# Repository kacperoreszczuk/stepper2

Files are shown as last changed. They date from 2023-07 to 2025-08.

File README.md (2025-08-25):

# stepper2
Second version of the lums stepper

Compiling in STM32CubeIDE:

0. Disclaimer: STM32CubeIDE constantly invents new ways to make this instruction not work. Be mentally prepared that you will have to bruteforce this with LLM anyway.
1. Install STM32CubeIDE, sadly requires account creation
2. Click "Import project" and select "fw" directory from this repository
3. In the "Project Explorer" panel on the left open stepper2.ioc
    - confirm "open associated perspecitve" if prompted
    - continue with the current version of the firmware if prompted (do not migrate)
    - Login into MyST account if prompted
    - if not prompted and you get problems later in the instruction in point 4  (more precisely "this project is not a CDT project") then in the stepper2.ioc window click Help->Configuration Tool->Manage Embedded Software Libraries, scroll to STM32H7 and check tick box near version 1.11.1. Click Install. Hopefully you will be prompted to login and the package will install. Continue with instruction (starting here with Project->Generate Code)
    - in the top menu select Project->Generate Code
    - confirm "open associated perspecitve" if prompted
4. go to Project -> Properties -> C/C++ Build -> Settings
    - if "Properties" button is inactive click on main.c file subwindow to focus on it
    - in MCU(or MCU/MPU) Settings  check both "Use float..." options
    - in "MCU Post build outputs" enable binary file (or "convert to binary file")
    - in MCU(or MCU/MPU) GCC Compiler->Optimization: change level to -O3
    - in MCU(or MCU/MPU) G++ Compiler->Optimization: change level to -O3
    - If you want to switch to release configuration, change configuration to Release in the top of the Settings window, and repeat last four steps. In that case take care to build in the release later.
    - click apply and close, confirm if prompted to rebuild index
5. You may want to go to Core/Inc/defaults.hpp and change #define DRIVER_ID to a different value (any you like), especially if you would use more than one device simultaneously and want to be able to discern between them when talking through serial port.
6. Power up the driver and connect it with micro usb port (near the power input socket, slightly lower). Click Run->Run or click the green arrow icon to build and flash the device.
    - You may be prompted to upgrade the stlink firmware. Agree. In the STLinkUpgrade Window click "Open in update mode" and then "Upgrade". Unplug and plug the micro USB cable and try again number 6 in this instruction.
    - you may be prompted to save the files you edited. Agree.
7. Alternatively to point 6. you can select Project->Build Project and then copy manually the file in Debug/stepper2.bin to the mass storage device that opens after conneting the driver.

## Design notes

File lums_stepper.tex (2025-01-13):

%

\documentclass[10pt,article]{article}
\usepackage[T1]{fontenc}
\usepackage[utf8]{inputenc}
\usepackage{graphicx}
\usepackage{hyperref}
\usepackage[font={small,it}]{caption}
\usepackage[a4paper,top=1.1cm,bottom=2cm,left=1.9cm,right=1.9cm]{geometry}
\usepackage{color, colortbl}
\usepackage{tabularx}
\usepackage{sectsty}
\usepackage{float}
\usepackage{hyperref}
\definecolor{Gray}{gray}{0.85}
\sectionfont{\huge}
\renewcommand{\familydefault}{\sfdefault}
\captionsetup{labelfont=bf}

\title{LUMS Stepper 2.0 -- universal 3-axis stepper motor controller}
\author{Kacper Oreszczuk}
\date{}
\begin{document}

\maketitle
 \section{Motivation}
Stepper motors are commonly used in laboratory. They are powering x-y-z translation stages, tunable filters, polarisation optics and many other devices. The goal of this project is to replace commercially available drivers with a cheaper, more reliable and more universal solution. 

\subsection*{Cost:}
Commercially available stepper motor drivers designed for laboratory use can reach prices
of a few hundred US\ Dollars for a single axis. Proposed solution costs about \$40 per axis with small
labour cost.

\subsection*{Quality:}
Personal experience in our laboratory revealed problems with microstep precision in drivers supplied by one of the leading laboratory equipment manufacturers. I have tested thoroughly stepper motor chip before choosing it for this project. 
\subsection*{Features:}
Custom solution allowed me to implement important additional features. The most important is automatic compensation of mechanical hysteresis.

\section{Hardware design}

Single device is able to control three bipolar stepper motors with 1/64 microsteps precision. Maximum current is about $2.0$\,A per motor and the supply voltage must be between $7$\,V and $24$\,V.
Low level motor driving operation  is performed by\textit{TMC2226} driver on \textit{Stepstick} breakout board. Three such drivers are connected to \textit{NUCLEO144}  board with \textit{STM32H723ZG} microcontroller. Nucleo board connected via on-board \textit{FT232RL}\ USB-UART controller to computer provides virtual serial port for communication and power for logic layer of device. Separate power connector is provided on main PCB for motor operation and six high-density D-SUB15 female connectors for motors and encoders. Full schematics of the device is presented in Figure \ref{schematics}. PCB board is double-sided. It is advised to order PCB with SMD\ assembly. See Figure \ref{pcb} for PCB layout.  The driver is confined in 3D-printed case (Figure \ref{case}) protecting it and allowing mounting to optic table. 
%Picture \ref{photo} shows assembled device with the top lid removed. 
Design files for PCB and case along with source code for microcontroller are available at project page: \url{github.com/kacperoreszczuk/stepper2/}. 

%\begin{figure}[h] \centering \includegraphics[width = 11.5cm]{photo.png}
%\caption {Assembled Stepper 2.0.} \label{photo}\end{figure}
\newpage
\section{Software and protocol}

Driver has two basic operation modes - movement with given velocity or movement to given position. In either of the cases the movement of motor is smoothed at starting and stopping. For user convenience speeds and positions are expressed in real units (for example millimeters in case of linear travel stage), not motor steps. End switches (limit switches) of different types are supported by this driver. They provide additional safety, as the driver will stop at the edge of the movement range of, for example, linear translation stage. Limit switches are also used to automatically calibrate absolute position of the stage.

When the mechanical setup of driven actuator is not completely rigid, the mechanical hysteresis can occur. Due to this effect real position of the  actuator depends on the direction from which set position is approached. In this project user can specify the amplitude od mechanical hysteresis. Algorithm will track previous movements and compensate the offsets in a manner transparent for the user.  

User can communicate with LUMS Stepper via virtual serial port provided by Nucleo board. Protocol of communication is based on single line plain-text commands initiated from computer and on single line reply from driver. For protocol description please refer to Table \ref{protocol}. Full list of accepted commands is presented in Table \ref{commands}

\begin{table}[ht]\centering
\begin{tabularx}{\textwidth}{lX}
\rowcolor[gray]{0.80} Command: & ID header value \textbackslash r \\
\rowcolor[gray]{0.95} ID & Single digit number – number of motor, counted from 0. Defaults to 0 if not specified.\\
\rowcolor[gray]{0.95} header & Two lower case characters specifying command type (see table \ref{commands}).\\
\rowcolor[gray]{0.95} value & Numerical argument (optional depending on command type). Defaults to 0 if not specified. \\
\rowcolor[gray]{0.95} \textbackslash r or \textbackslash n\ & Any endline character. Other whitespace before, after or between command parts is ignored. \\
\rowcolor[gray]{0.80} Reply: & header value \textbackslash r\\
\rowcolor[gray]{0.95} header & Driver returns header after every command \\
\rowcolor[gray]{0.95} value & Optional depending on command type\\
\rowcolor[gray]{0.80} Error reply: & ?\textbackslash r\\
\end{tabularx}
\caption{Protocol of communication between PC and LUMS\ Stepper 2.0.}\label{protocol}
\end{table}

\begin{table}[ht] \centering
\begin{tabularx}{\textwidth}{lllX}
\rowcolor[gray]{0.80} Command & Abbreviation origin & Example & Description\\
\rowcolor[gray]{0.90} id & ID & id & Returns unique ID of device, between 101 and 199.\\
\rowcolor[gray]{0.95} ac & Axis Count & ac & Returns number of supported motors.\\
\rowcolor[gray]{0.90} sc & Set Current & 0sc600 &Sets motor current, in milliamperes.\\
\rowcolor[gray]{0.95} ss & Set Step & 0ss0.005 & Defines the size of motor full step in user units, for example in millimetres or degrees. \\
\rowcolor[gray]{0.90} sh & Set Hysteresis & 0sh0.001 & Sets mechanical hysteresis compensation distance. Algorithm applies corrections to target positions when necessary (f. eg. when changing direction). \\
\rowcolor[gray]{0.95} sm & Set Max Velocity & 0sm1.5 & Sets maximum allowed velocity in move velocity mode, in user units. \\
\rowcolor[gray]{0.90} sv & Set Velocity & 0sv1 & Sets velocity in move absolute mode, in user units. \\
\rowcolor[gray]{0.95} sa & Set Acceleration & 0sa0.5 & Sets time that it takes to accelerate from zero to move absolute velocity. \\
\rowcolor[gray]{0.90} sl & Set Limit & 0sl2 & Sets limit switch type. 0 – no limit switch, 1 - active limit switch (active high). 2/3 – mechanical, default NC/C. 4/5 similarly to 2/3, but enabled only for homing. \\
\rowcolor[gray]{0.95} sr & Set Reversed & 0sr1 & Reverses direction of motor rotation and swaps limit switches. \\
\rowcolor[gray]{0.90} so & Set Offset & 0so4.2 & Specifies the true position of the limit switch in user units. \\
\rowcolor[gray]{0.95} hm & HoMe & 0hm & Starts homing procedure. If limit type is set to zero, then it only corrects current position to be zero. \\
\rowcolor[gray]{0.90} hr & Homing Reversed & 0hr1 & Specifies if homing should be performed to rear limit switch (0, default) or to front limit switch (1).\\
\rowcolor[gray]{0.95} mv & Move Velocity & 0mv0.5 & Sets target velocity. Driver will smoothly increase or decrease speed to given value. \\
\rowcolor[gray]{0.90} ma & Move Absolute & 0ma3.2 & Sets target position. Driver will smoothly start and halt motor to achieve goal position. \\
\rowcolor[gray]{0.95} mr & Move Relative & 0mr0.1 & Changes target position by given value, even if target position was not achieved yet. In „move velocity” mode sets target relative to current position. \\
\rowcolor[gray]{0.90} tp & Tell Position & 0tp & Returns current position of given axis. \\
\rowcolor[gray]{0.95} ts & Tell Status & 0ts & Returns status of current axis. 0 – stopped, 1 – move velocity, 2 - move position, 3 – homing. \\
\rowcolor[gray]{0.90} ta & Tell All & ta & Returns current positions of all axes, separated by spaces. Next, after another space, returns statuses of all axes in single joined string.\\
\rowcolor[gray]{0.95} er & Encoder Raw & 0er & Returns encoder position in raw counts.\\
\rowcolor[gray]{0.90} es & Encoder Step & 0es0.002 & Configures encoder step in user units. Must be called after configuring motor step.\\
\rowcolor[gray]{0.95} ep & Encoder Position & 0ep & Returns encoder position in user units. \\
\rowcolor[gray]{0.90} ds & Driver Status & 0ds & Returns the TMC's DRV\_STATUS register in hex format. See TMC2226 datasheet, table 5.5.3 for details. \\
\rowcolor[gray]{0.95} dr & Driver Reset & 0dr & Cycles the EN pin of the TMC driver, clearing the hardware error flags in the process. \\
\rowcolor[gray]{0.90} tt & Tell Time & tt & Returns time from boot in seconds. \\
\end{tabularx}
\caption{Commands in communication protocol.}\label{commands}
\end{table}

\begin{figure}[H]
 \centering
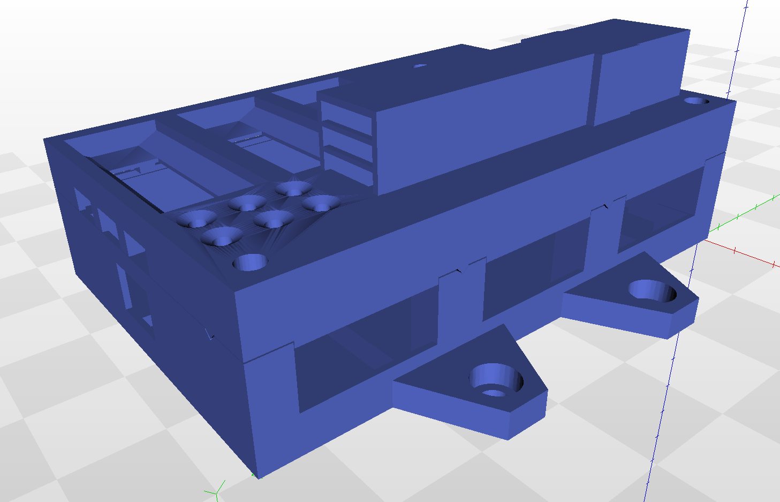
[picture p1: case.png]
 
\caption {Case, model for 3D printer.} \label{case}
\end{figure}

\begin{figure}[h]
 \centering
 
\caption {Schematics of the LUMS stepper.} \label{schematics}
\end{figure}

\begin{figure}[h]
 \centering
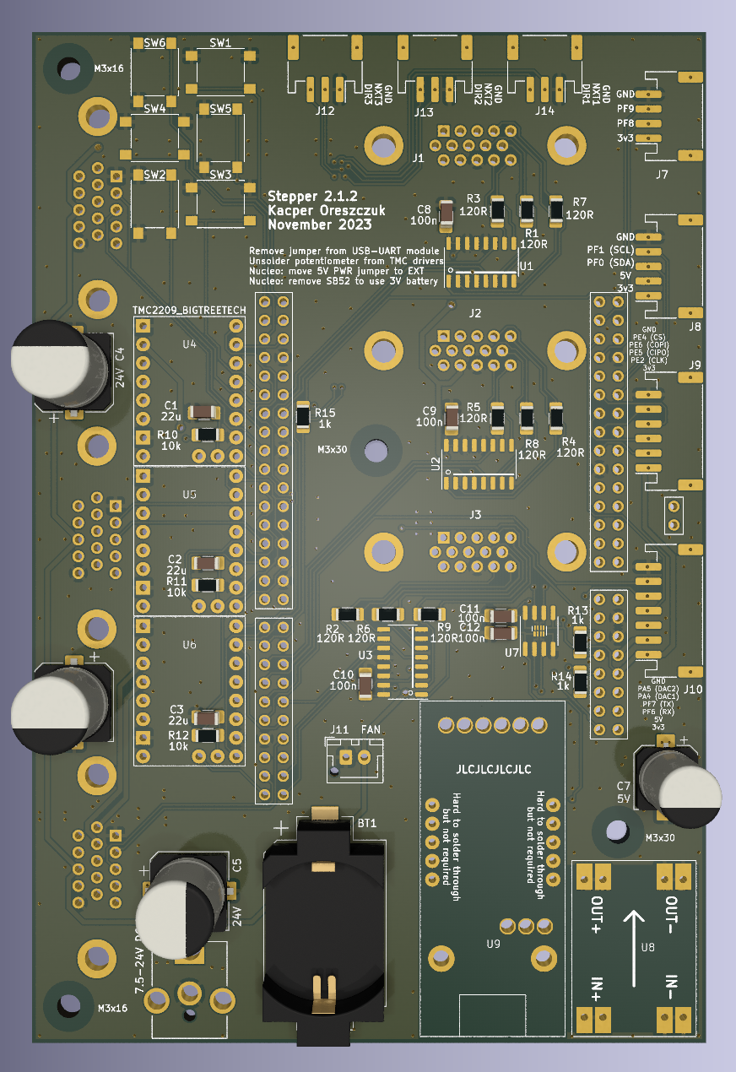
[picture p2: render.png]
 
\caption {PCB design. View from top.} \label{pcb}
\end{figure}

\newpage
\section{How to set-up Stepper 2.0 in pyLUMS software}
This section is very specific to LUMS laboratory.

In order to control Stepper 2.0 from pyLUMS software, you need to configure it in \texttt{local\_devices.ini} and \texttt{devices.ini} file. Most of the work is put in the former one. Here is example of the relevant entry in \texttt{local\_devices.ini} file:

\begin{verbatim}
[stepperdevice]
name = My Stepper
class = misc.stepper.StepperWorker
req_port = 7040   
pub_port = 7041
id = LUMS01
current = 800,800,800
step = 0.005,0.005,0.005
encoder_step = 0.0001,0.0001,0.0001
velocity = 3,3,3
max_velocity = 3,3,3
hysteresis = 0.0012,0.0012,0.0012
homing_offset = 0,0,0
limit_type = 3,3,3
reversed = 0,1,1
acceleration_time = 0.20,0.20,0.20
\end{verbatim}

The meaning of each parameter is described in the table \ref{localdevicesini}.

\begin{table}[H]\centering
\begin{tabularx}{\textwidth}{lX}
\rowcolor[gray]{0.80} Parameter: & Description  \\
\rowcolor[gray]{0.95} id & The id of the given driver. \vspace{2mm} \\
\rowcolor[gray]{0.95} current & (for each axis) Move current (in mA) At rest the current is automatically reduced. \vspace{2mm} \\
\rowcolor[gray]{0.95} step & (for each axis) The distance in the user units corresponding to a single motor step. It does not directly affect the driver, only the values presented to the user.\vspace{2mm} \\
\rowcolor[gray]{0.95} encoder\_step & (optional, for each axis) Distance between encoder marks in the user units. It is relevant only for the stages fitted with the encoder.  \vspace{2mm} \\
\rowcolor[gray]{0.95} velocity  & (for each axis) Default move velocity in the user units per second. Note the user can request moving with different velocity.  \\
\rowcolor[gray]{0.95} max\_velocity & (for each axis) Maximum move velocity in user units per second for each axis. The software will prohibit the user to go beyond this value. \\
\rowcolor[gray]{0.95} hysteresis & (optional, for each axis) ... \vspace{2mm} \\
\rowcolor[gray]{0.95} homing\_offset & (optional, for each axis) ... \vspace{2mm} \\
\rowcolor[gray]{0.95} limit\_type & (optional, for each axis) Definition of the limit switches. Possible options: 0 -- no limit switches, ...  \vspace{2mm} \\
\rowcolor[gray]{0.95} acceleration\_time & (optional, for each axis) Time in seconds to smoothly reach the moving velocity. \vspace{2mm} \\
\end{tabularx}
\caption{Parameters specified in \texttt{local\_devices.ini} file if you use pyLUMS software}\label{localdevicesini}
\end{table}

Compared to multiple parameters defined above, the configuration in \texttt{devices.ini}  file is relatively simple. Basically you need to match the number of the ports, e.g.:
\begin{verbatim}
[stepper]
class = misc.stepper.Stepper
req_port = 7040
pub_port = 7041
\end{verbatim}

%\begin{thebibliography}{99}
%\bibitem{Kopp} Arnold Kopp et. al. Natura 6 (2018)
%\end{thebibliography}

\end{document}

\grid

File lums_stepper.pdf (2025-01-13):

# LUMS Stepper 2.0 universal 3-axis stepper motor controller

### Kacper Oreszczuk

# 1 Motivation

Stepper motors are commonly used in laboratory. They are powering x-y-z translation stages, tunable lters, polarisation optics and many other devices. The goal of this project is to replace commercially available drivers with a cheaper, more reliable and more universal solution.

### Cost:

Commercially available stepper motor drivers designed for laboratory use can reach prices of a few hundred US Dollars for a single axis. Proposed solution costs about $40 per axis with small labour cost.

### Quality:

Personal experience in our laboratory revealed problems with microstep precision in drivers supplied by one of the leading laboratory equipment manufacturers. I have tested thoroughly stepper motor chip before choosing it for this project.

### Features:

Custom solution allowed me to implement important additional features. The most important is automatic compensation of mechanical hysteresis.

# 2 Hardware design

Single device is able to control three bipolar stepper motors with 1/64 microsteps precision. Maximum current is about 2.0A per motor and the supply voltage must be between 7V and 24V. Low level motor driving operation is performed byTMC2226 driver on Stepstick breakout board. Three such drivers are connected to NUCLEO144 board with STM32H723ZG microcontroller. Nucleo board connected via on-board FT232RL USB-UART controller to computer provides virtual serial port for communication and power for logic layer of device. Separate power connector is provided on main PCB for motor operation and six high-density D-SUB15 female connectors for motors and encoders. Full schematics of the device is presented in Figure 2. PCB board is double-sided. It is advised to order PCB with SMD assembly. See Figure 3 for PCB layout. The driver is conned in 3D-printed case (Figure 1) protecting it and allowing mounting to optic table. Design les for PCB and case along with source code for microcontroller are available at project page: github.com/kacperoreszczuk/stepper2/.

# 3 Software and protocol

Driver has two basic operation modes - movement with given velocity or movement to given position. In either of the cases the movement of motor is smoothed at starting and stopping. For user convenience speeds and positions are expressed in real units (for example millimeters in case of linear travel stage), not motor steps. End switches (limit switches) of dierent types are supported by this driver. They provide additional safety, as the driver will stop at the edge of the movement range of, for example, linear translation stage. Limit switches are also used to automatically calibrate absolute position of the stage.
| When the mechanical setup of driven actuator is not completely rigid, the mechanical hysteresis can occur. Due to
this eect real position of the actuator depends on the direction from which set position is approached. In this project user can specify the amplitude od mechanical hysteresis. Algorithm will track previous movements and compensate the osets in a manner transparent for the user.
| User can communicate with LUMS Stepper via virtual serial port provided by Nucleo board. Protocol of commu-
nication is based on single line plain-text commands initiated from computer and on single line reply from driver. For protocol description please refer to Table 1. Full list of accepted commands is presented in Table 2
Command: | ID header value \r
ID | Single digit number number of motor, counted from 0. Defaults to 0 if not specied.
header | Two lower case characters specifying command type (see table 2).
value | Numerical argument (optional depending on command type). Defaults to 0 if not specied.
\r or \n | Any endline character. Other whitespace before, after or between command parts is ignored.
Reply: | header value \r
header | Driver returns header after every command
value | Optional depending on command type
Error reply: | ?\r

Table 1: Protocol of communication between PC and LUMS Stepper 2.0.

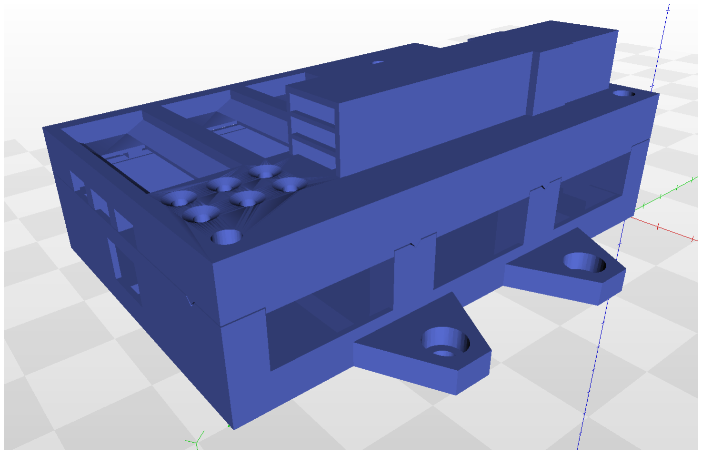
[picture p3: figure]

Figure 1: Case, model for 3D printer.

# +3V3 SW2 SW_Push H1 MountingHole GND

# VCC GND

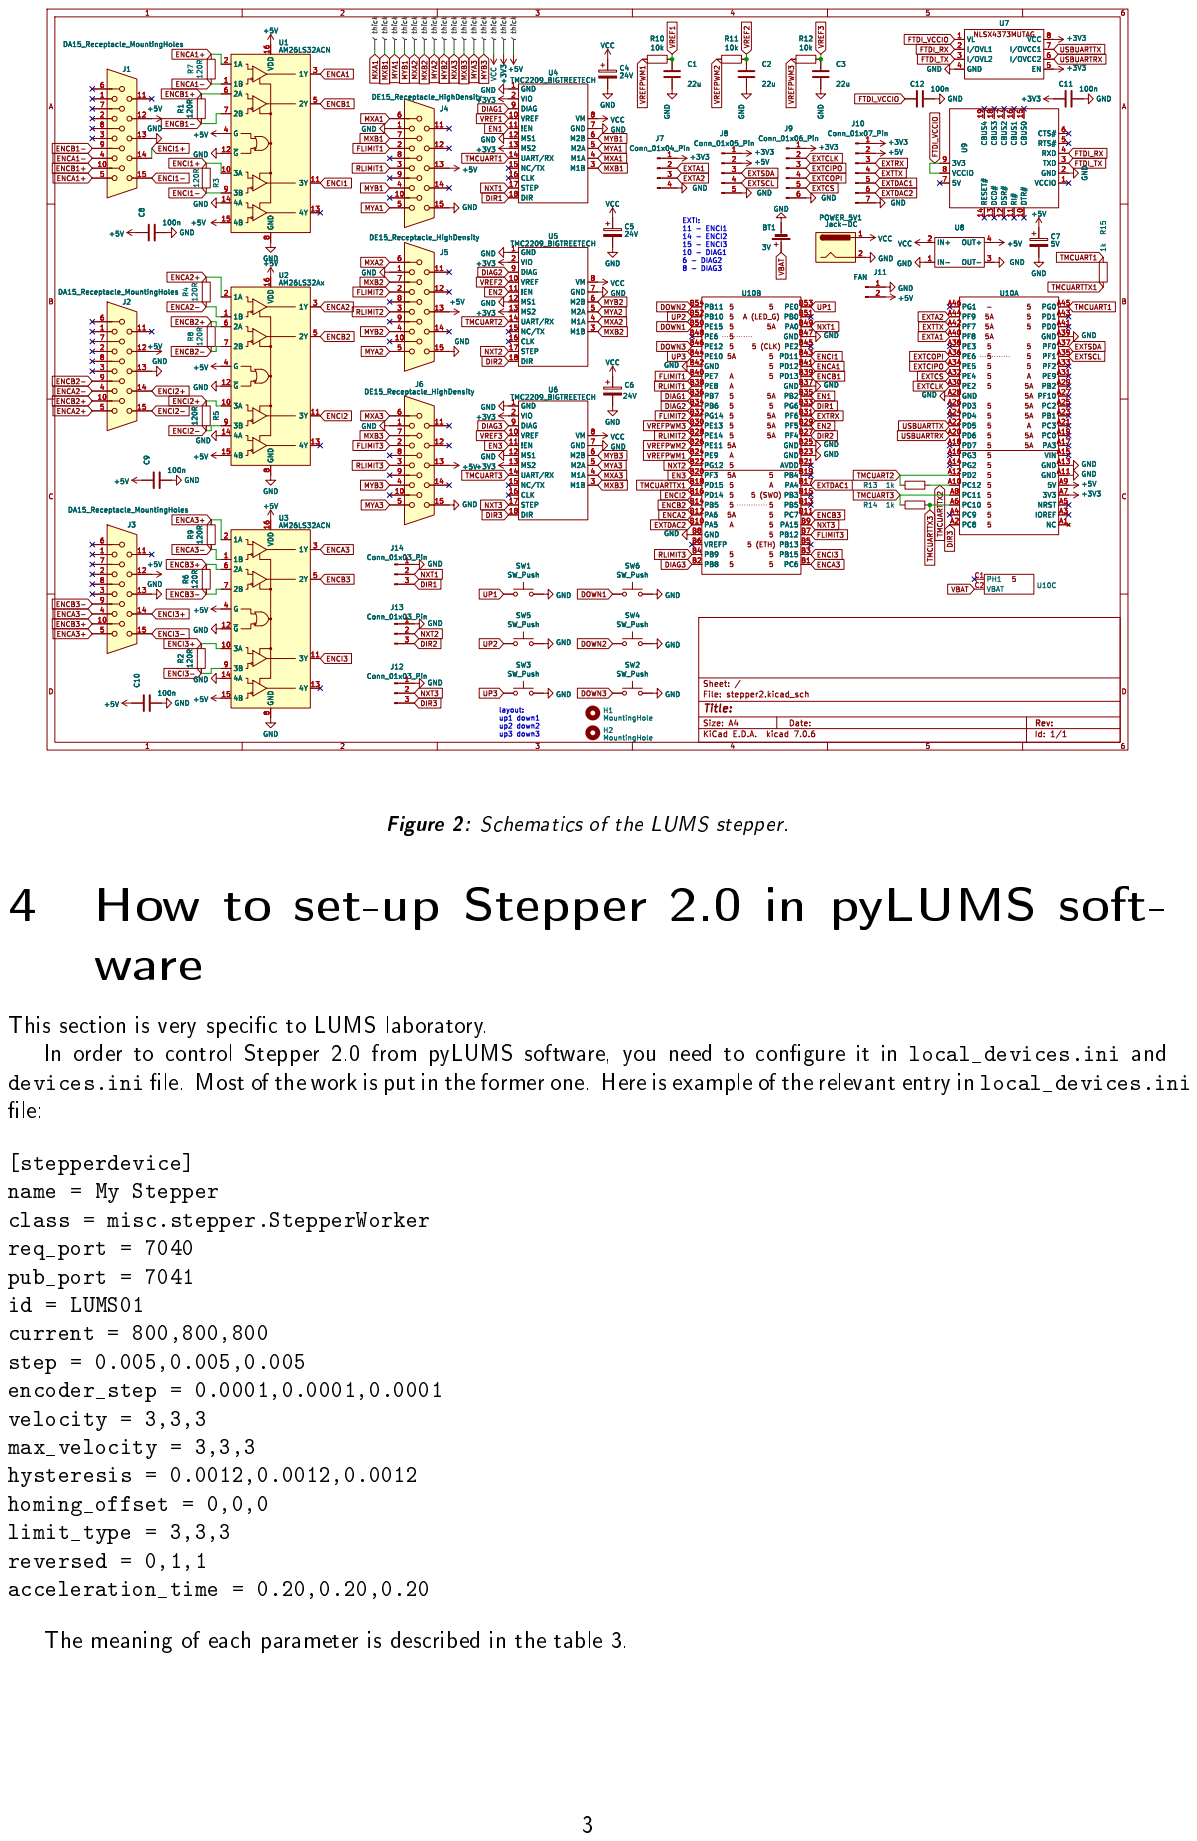
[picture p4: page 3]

Id: 1/1 Title: File: stepper2.kicad_sch Sheet: /

Figure 2: Schematics of the LUMS stepper.

This section is very specic to LUMS laboratory.
In order to control Stepper 2.0 from pyLUMS software, you need to congure it in local_devices.ini and
devices.ini le. Most of the work is put in the former one. Here is example of the relevant entry in local_devices.ini

The meaning of each parameter is described in the table 3.

Parameter: | Description
id | The id of the given driver.
current | (for each axis) Move current (in mA) At rest the current is automatically reduced.
step | (for each axis) The distance in the user units corresponding to a single motor step. It does not directly aect the driver, only the values presented to the user.
encoder_step | (optional, for each axis) Distance between encoder marks in the user units. It is relevant only for the stages tted with the encoder.
velocity | (for each axis) Default move velocity in the user units per second. Note the user can request moving with dierent velocity.
max_velocity | (for each axis) Maximum move velocity in user units per second for each axis. The software will prohibit the user to go beyond this value.
hysteresis | (optional, for each axis) ...
homing_oset | (optional, for each axis) ...
limit_type | (optional, for each axis) Denition of the limit switches. Possible options: 0 no limit switches, ...
acceleration_time | (optional, for each axis) Time in seconds to smoothly reach the moving velocity.

Table 3: Parameters specied in local_devices.ini le if you use pyLUMS software

Compared to multiple parameters dened above, the conguration in devices.ini le is relatively simple. Basically you need to match the number of the ports, e.g.:

[stepper]
class = misc.stepper.Stepper
req_port = 7040
pub_port = 7041

Command | Abbreviation origin | Example | Description
id | ID | id | Returns unique ID of device, between 101 and 199.
ac | Axis Count | ac | Returns number of supported motors.
sc | Set Current | 0sc600 | Sets motor current, in milliamperes.
ss | Set Step | 0ss0.005 | Denes the size of motor full step in user units, for example in mil-limetres or degrees.
sh | Set Hysteresis | 0sh0.001 | Sets mechanical hysteresis compensation distance. Algorithm applies corrections to target positions when necessary (f. eg. when changing direction).
sm | Set Max Velocity | 0sm1.5 | Sets maximum allowed velocity in move velocity mode, in user units.
sv | Set Velocity | 0sv1 | Sets velocity in move absolute mode, in user units.
sa | Set Acceleration | 0sa0.5 | Sets time that it takes to accelerate from zero to move absolute velocity.
sl | Set Limit | 0sl2 | Sets limit switch type. 0 no limit switch, 1 - active limit switch (active high). 2/3 mechanical, default NC/C. 4/5 similarly to 2/3, but enabled only for homing.
sr | Set Reversed | 0sr1 | Reverses direction of motor rotation and swaps limit switches.
so | Set Oset | 0so4.2 | Species the true position of the limit switch in user units.
hm | HoMe | 0hm | Starts homing procedure. If limit type is set to zero, then it only corrects current position to be zero.
hr | Homing Reversed | 0hr1 | Species if homing should be performed to rear limit switch (0, de-fault) or to front limit switch (1).
mv | Move Velocity | 0mv0.5 | Sets target velocity. Driver will smoothly increase or decrease speed to given value.
ma | Move Absolute | 0ma3.2 | Sets target position. Driver will smoothly start and halt motor to achieve goal position.
mr | Move Relative | 0mr0.1 | Changes target position by given value, even if target position was not achieved yet. In move velocity mode sets target relative to current position.
tp | Tell Position | 0tp | Returns current position of given axis.
ts | Tell Status | 0ts | Returns status of current axis. 0 stopped, 1 move velocity, 2 -move position, 3 homing.
ta | Tell All | ta | Returns current positions of all axes, separated by spaces. Next, after another space, returns statuses of all axes in single joined string.
er | Encoder Raw | 0er | Returns encoder position in raw counts.
es | Encoder Step | 0es0.002 | Congures encoder step in user units. Must be called after congur-ing motor step.
ep | Encoder Position | 0ep | Returns encoder position in user units.
ds | Driver Status | 0ds | Returns the TMC's DRV_STATUS register in hex format. See TMC2226 datasheet, table 5.5.3 for details.
dr | Driver Reset | 0dr | Cycles the EN pin of the TMC driver, clearing the hardware error ags in the process.
tt | Tell Time | tt | Returns time from boot in seconds.

Table 2: Commands in communication protocol.

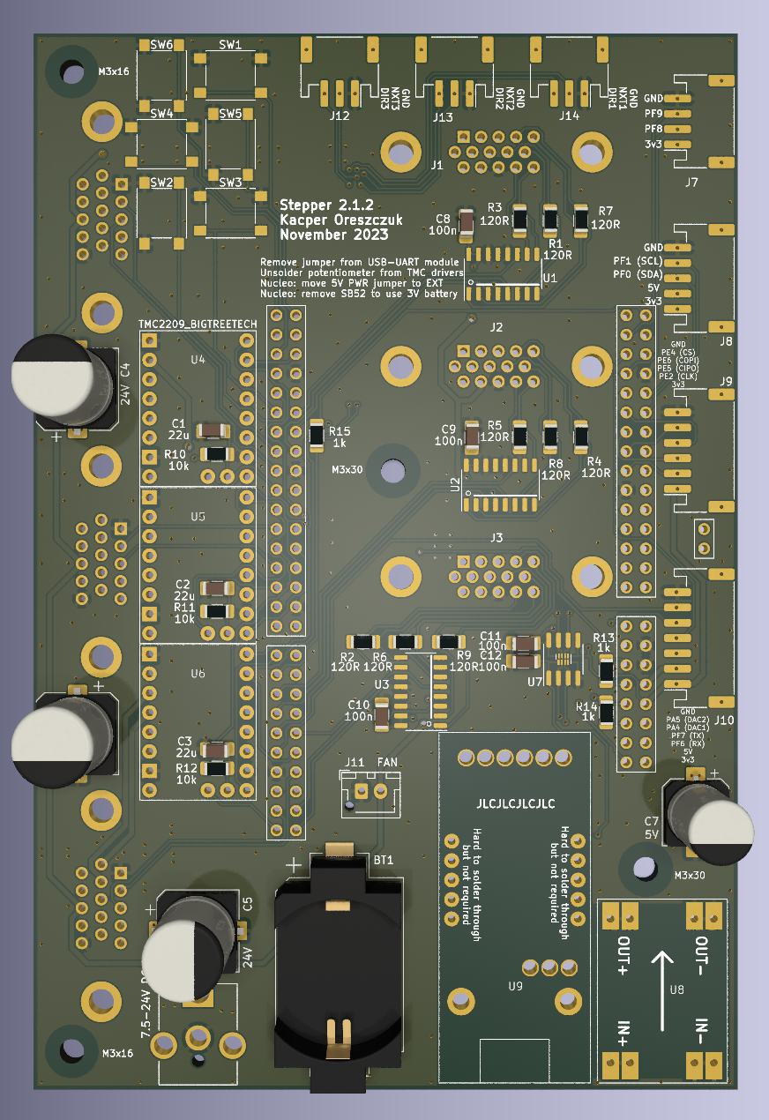
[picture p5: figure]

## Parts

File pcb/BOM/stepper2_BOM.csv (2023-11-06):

Comment | Designator | Footprint | LCSC
3V | BT1 | Battery:BatteryHolder_Keystone_1060_1x2032
22u | C1 | Capacitor_SMD:C_1206_3216Metric_Pad1.33x1.80mm_HandSolder | C12891
22u | C2 | Capacitor_SMD:C_1206_3216Metric_Pad1.33x1.80mm_HandSolder | C12891
22u | C3 | Capacitor_SMD:C_1206_3216Metric_Pad1.33x1.80mm_HandSolder | C12891
24V | C4 | Capacitor_SMD:CP_Elec_10x10.5 | C2880403
24V | C5 | Capacitor_SMD:CP_Elec_10x10.5 | C2880403
24V | C6 | Capacitor_SMD:CP_Elec_10x10.5 | C2880403
5V | C7 | Capacitor_SMD:CP_Elec_8x10.5 | C310836
100n | C8 | Capacitor_SMD:C_1206_3216Metric_Pad1.33x1.80mm_HandSolder | C24497
100n | C9 | Capacitor_SMD:C_1206_3216Metric_Pad1.33x1.80mm_HandSolder | C24497
100n | C10 | Capacitor_SMD:C_1206_3216Metric_Pad1.33x1.80mm_HandSolder | C24497
100n | C11 | Capacitor_SMD:C_1206_3216Metric_Pad1.33x1.80mm_HandSolder | C24497
100n | C12 | Capacitor_SMD:C_1206_3216Metric_Pad1.33x1.80mm_HandSolder | C24497
MountingHole | H1 | stepper2:MountingHole_3.2mm_M3
MountingHole | H2 | stepper2:MountingHole_3.2mm_M3
DA15_Receptacle_MountingHoles | J1 | stepper2:DSUB-15-HD_Vertical_Pitch2.29x1.98mm_Mercury3000_Enc
DA15_Receptacle_MountingHoles | J2 | stepper2:DSUB-15-HD_Vertical_Pitch2.29x1.98mm_Mercury3000_Enc
DA15_Receptacle_MountingHoles | J3 | stepper2:DSUB-15-HD_Vertical_Pitch2.29x1.98mm_Mercury3000_Enc
DE15_Receptacle_HighDensity | J4 | stepper2:DSUB-15-HD_Horizontal_Pitch2.29x2.54mm_EdgePinOffset9.40mm
DE15_Receptacle_HighDensity | J5 | stepper2:DSUB-15-HD_Horizontal_Pitch2.29x2.54mm_EdgePinOffset9.40mm
DE15_Receptacle_HighDensity | J6 | stepper2:DSUB-15-HD_Horizontal_Pitch2.29x2.54mm_EdgePinOffset9.40mm
Conn_01x04_Pin | J7 | stepper2:JST_PH_S4B-PH-SM4-TB_1x04-1MP_P2.00mm_Horizontal | C265102
Conn_01x05_Pin | J8 | stepper2:JST_PH_S5B-PH-SM4-TB_1x05-1MP_P2.00mm_Horizontal | C265104
Conn_01x06_Pin | J9 | stepper2:JST_PH_S6B-PH-SM4-TB_1x06-1MP_P2.00mm_Horizontal | C265405
Conn_01x07_Pin | J10 | stepper2:JST_PH_S7B-PH-SM4-TB_1x07-1MP_P2.00mm_Horizontal | C265453
FAN | J11 | Connector_JST:JST_XH_B2B-XH-AM_1x02_P2.50mm_Vertical
Conn_01x03_Pin | J12 | stepper2:JST_PH_S3B-PH-SM4-TB_1x03-1MP_P2.00mm_Horizontal | C265101
Conn_01x03_Pin | J13 | stepper2:JST_PH_S3B-PH-SM4-TB_1x03-1MP_P2.00mm_Horizontal | C265101
Conn_01x03_Pin | J14 | stepper2:JST_PH_S3B-PH-SM4-TB_1x03-1MP_P2.00mm_Horizontal | C265101
Jack-DC | POWER_5V1 | Connector_BarrelJack:BarrelJack_CUI_PJ-063AH_Horizontal_CircularHoles
120R | R1 | Resistor_SMD:R_1206_3216Metric_Pad1.30x1.75mm_HandSolder | C17909
120R | R2 | Resistor_SMD:R_1206_3216Metric_Pad1.30x1.75mm_HandSolder | C17909
120R | R3 | Resistor_SMD:R_1206_3216Metric_Pad1.30x1.75mm_HandSolder | C17909
120R | R4 | Resistor_SMD:R_1206_3216Metric_Pad1.30x1.75mm_HandSolder | C17909
120R | R5 | Resistor_SMD:R_1206_3216Metric_Pad1.30x1.75mm_HandSolder | C17909
120R | R6 | Resistor_SMD:R_1206_3216Metric_Pad1.30x1.75mm_HandSolder | C17909
120R | R7 | Resistor_SMD:R_1206_3216Metric_Pad1.30x1.75mm_HandSolder | C17909
120R | R8 | Resistor_SMD:R_1206_3216Metric_Pad1.30x1.75mm_HandSolder | C17909
120R | R9 | Resistor_SMD:R_1206_3216Metric_Pad1.30x1.75mm_HandSolder | C17909
10k | R10 | Resistor_SMD:R_1206_3216Metric_Pad1.30x1.75mm_HandSolder | C17902
10k | R11 | Resistor_SMD:R_1206_3216Metric_Pad1.30x1.75mm_HandSolder | C17902
10k | R12 | Resistor_SMD:R_1206_3216Metric_Pad1.30x1.75mm_HandSolder | C17902
1k | R13 | Resistor_SMD:R_1206_3216Metric_Pad1.30x1.75mm_HandSolder | C4410
1k | R14 | Resistor_SMD:R_1206_3216Metric_Pad1.30x1.75mm_HandSolder | C4410
1k | R15 | Resistor_SMD:R_1206_3216Metric_Pad1.30x1.75mm_HandSolder | C4410
SW_Push | SW1 | Button_Switch_SMD:SW_Push_1P1T_NO_6x6mm_H9.5mm | C620327
SW_Push | SW2 | Button_Switch_SMD:SW_Push_1P1T_NO_6x6mm_H9.5mm | C620327
SW_Push | SW3 | Button_Switch_SMD:SW_Push_1P1T_NO_6x6mm_H9.5mm | C620327
SW_Push | SW4 | Button_Switch_SMD:SW_Push_1P1T_NO_6x6mm_H9.5mm | C620327
SW_Push | SW5 | Button_Switch_SMD:SW_Push_1P1T_NO_6x6mm_H9.5mm | C620327
SW_Push | SW6 | Button_Switch_SMD:SW_Push_1P1T_NO_6x6mm_H9.5mm | C620327
AM26LS32ACN | U1 | stepper2:SO-16_3.9x9.9mm_P1.27mm | C19092
AM26LS32Ax | U2 | stepper2:SO-16_3.9x9.9mm_P1.27mm | C19092
AM26LS32ACN | U3 | stepper2:SO-16_3.9x9.9mm_P1.27mm | C19092
TMC2209_BIGTREETECH | U4 | stepper2:TMC2209_BIGTREETECH
TMC2209_BIGTREETECH | U5 | stepper2:TMC2209_BIGTREETECH
TMC2209_BIGTREETECH | U6 | stepper2:TMC2209_BIGTREETECH
~ | U7 | stepper2:UDFN-8_1.2x1.8mm_OR_SO8_3.9x4.9mm | C604194
~ | U8 | stepper2:DCDC_17.0mm_22.2mm
~ | U9 | stepper2:Waveshare_FT232_USBC_module
~ | U10 | stepper2:Nucleo144_H723_withVBAT

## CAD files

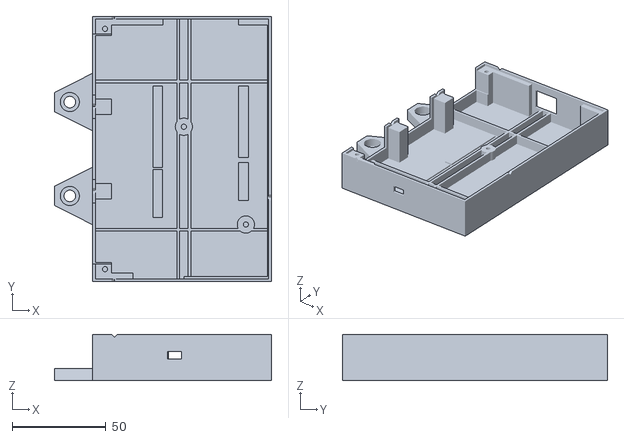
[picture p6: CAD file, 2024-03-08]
case/bottom.stl
115.6 x 141.3 x 24.5

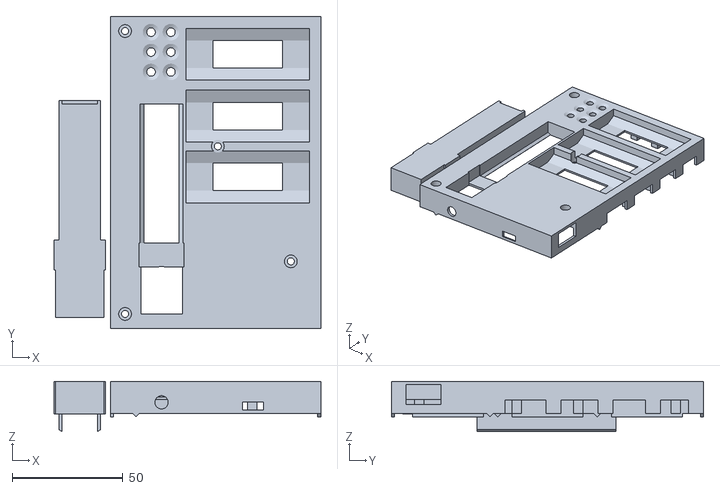
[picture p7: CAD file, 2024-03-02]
case/top.stl
120.8 x 141.3 x 22.8

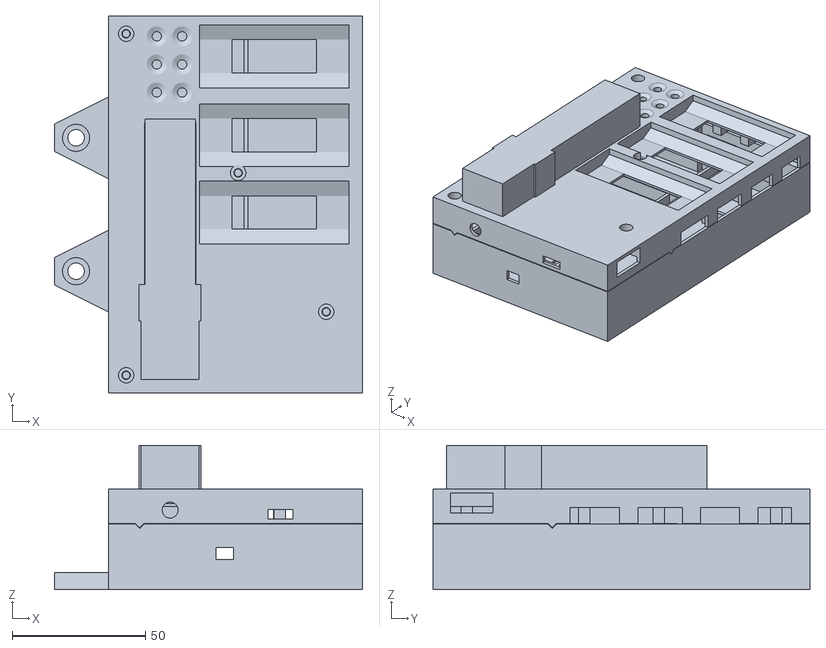
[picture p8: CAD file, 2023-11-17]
case/all_render.stl
115.6 x 141.3 x 54.1

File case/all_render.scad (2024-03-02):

include <top.scad>
include <bottom.scad>


base_bottom();
translate([0, 0, d + thickness_below_pcb + pcb_thickness + 0.3])
    union () {
        base();
        corridor_top();
    }

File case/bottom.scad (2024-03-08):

include <common.scad>

module pcb_support_2d() {
    left_square_pad_size = 8.5;
    left_midpoint_y_1 = 46.5;
    left_midpoint_y_2 = 91.5;
    top_left_bar_len = 36;
    top_right_bar_len = 16;
    top_bar_width = 3;
    right_bar_width = 0.5;
    bottom_left_bar_len = 20;
    bottom_left_bar_width = 3;
    bottom_right_bar_len = 45;
    bottom_right_bar_width = 1.2;
    union() {
        
        translate ([-pcb_margin, -pcb_margin]) 
            square(pcb_margin + left_square_pad_size);
        translate ([-pcb_margin, pcb_y - left_square_pad_size]) 
            square(pcb_margin + left_square_pad_size);
        translate ([-pcb_margin, left_midpoint_y_1 - left_square_pad_size / 2]) 
            square([pcb_margin + left_square_pad_size, left_square_pad_size]);
        translate ([-pcb_margin, left_midpoint_y_2 - left_square_pad_size / 2]) 
            square([pcb_margin + left_square_pad_size, left_square_pad_size]);
        
        translate ([-pcb_margin, pcb_y - top_bar_width]) 
            square([pcb_margin + top_left_bar_len, pcb_margin + top_bar_width]);
        translate ([pcb_x - top_right_bar_len, pcb_y - top_bar_width]) 
            square([pcb_margin + top_right_bar_len, pcb_margin + top_bar_width]);
        
        translate ([pcb_x - right_bar_width, -pcb_margin]) 
            square([pcb_margin + right_bar_width, pcb_y + 2 * pcb_margin]);
        
        
        translate ([-pcb_margin, -pcb_margin]) 
            square([pcb_margin + bottom_left_bar_len, pcb_margin + bottom_left_bar_width]);
        translate ([pcb_x - bottom_right_bar_len, -pcb_margin]) 
            square([pcb_margin + bottom_right_bar_len, pcb_margin + bottom_right_bar_width]);
    }
}

module base_2d_bottom() {
    translate([-d - pcb_margin, -d - pcb_margin])
        square([pcb_x + 2 * pcb_margin + 2 * d, pcb_y + 2 * pcb_margin + 2 * d]);
}

module outer_frame_2d_bottom() {
    difference() {
        base_2d_bottom();
        translate([-pcb_margin, -pcb_margin])
            square([pcb_x + 2 * pcb_margin, pcb_y + 2 * pcb_margin]);
    }
}

module structure_rails_2d() {
    rail_vertical_x_1 = 44;
    rail_vertical_x_2 = 50;
    rail_horizontal_y_1 = 26;
    rail_horizontal_y_2 = 105;
    union() {
        translate([-pcb_margin, rail_horizontal_y_1 - d / 2])
            square([pcb_x + 2 * pcb_margin, d]);
        translate([-pcb_margin, rail_horizontal_y_2 - d / 2])
            square([pcb_x + 2 * pcb_margin, d]);
        translate([rail_vertical_x_1 - d / 2, -pcb_margin])
            square([d, pcb_y + 2 * pcb_margin]);
        translate([rail_vertical_x_2 - d / 2, -pcb_margin])
            square([d, pcb_y + 2 * pcb_margin]);
    }
}

module support_nucleo_pins_2d() {
    x1 = 30.47;
    y1 = 32.6;
    w1 = 5.08;
    h1 = 25.4;
    
    x2 = 30.47;
    y2 = 59.27;
    w2 = 5.08;
    h2 = 43.18;
    
    x3 = 76.19;
    y3 = 41.49;
    w3 = 5.08;
    h3 = 20.33;
    
    x4 = 76.19;
    y4 = 64.35;
    w4 = 5.08;
    h4 = 38.10;
    
    
    union() {
        translate([x1, y1])
            square([w1, h1]);
        translate([x2, y2])
            square([w2, h2]);
        translate([x3, y3])
            square([w3, h3]);
        translate([x4, y4])
            square([w4, h4]);
    }
}

module motor_cutouts_2d() {  // in yz plane
    depth = 14.9;
    union() {
        for (i=[0, 1, 2])
        translate([motor_port_y[i] - motor_width / 2, d + thickness_below_pcb + pcb_thickness - depth])
            square([motor_width, depth + 1]);
    }
}

module m3_mount_base() {
    for (i=[2, 3]) 
        translate([m3_x[i], m3_y[i], 0])
            cylinder(d=m3_mount_diameter, h=d+m3_mount_h);
}

module m3_mount_drills() {
    for (i=[0, 1, 2, 3]) 
        translate([m3_x[i], m3_y[i], d])
            cylinder(d=m3_drill_diameter, h=thickness_below_pcb + pcb_thickness);
}

module mount_tab(yyy) {
    head_diameter = 10.2;
    drill_offset = head_diameter / 2 + 7;
    drill_diameter = 6.2;
    base_thickness = 5 + d;
    
   
    translate([-d-pcb_margin, yyy, 0])
        difference() {
            linear_extrude(height=base_thickness) 
                polygon([
                [0, -head_diameter * 1.5], 
                [-drill_offset - head_diameter * 0.8, -head_diameter / 2],
                [-drill_offset - head_diameter * 0.8, head_diameter / 2],
                [0, head_diameter * 1.5]       
            ]);
            translate([-drill_offset, 0, d])
                cylinder(h=100, d=head_diameter);
            translate([-drill_offset, 0, -1])
                cylinder(h=100, d=drill_diameter);
        }
}


module stlink_drill() {
    x = 42;
    depth = 9.5;
    w = 7.5;
    h = 4.0;
    translate([x, -pcb_margin - d / 2, d + thickness_below_pcb - depth])
        cube([w, 10, h], center=true);
}

module ethernet_drill() {
    x = 46.85;
    depth = 9.5;
    w = 16.25;
    h = 12;
    translate([x, pcb_y + pcb_margin + d / 2, d + thickness_below_pcb - depth])
        cube([w, 10, h], center=true);
}

module base_bottom() {
    difference() {
        union() {
            linear_extrude(d)
                base_2d_bottom();
            linear_extrude(d + thickness_below_pcb)
                pcb_support_2d();
            linear_extrude(d + thickness_below_pcb + pcb_thickness)
                outer_frame_2d_bottom();
            linear_extrude(d + structure_rails_height)
                structure_rails_2d();
            linear_extrude(d + support_nucleo_pins_h)
                support_nucleo_pins_2d();
            m3_mount_base();
            mount_tab(pcb_y / 2 - 25);
            mount_tab(pcb_y / 2 + 25);
        }
        rotate(90, [1, 0, 0]) 
            rotate(90, [0, 1, 0])
                linear_extrude(17, center=true)
                    motor_cutouts_2d();
        m3_mount_drills();
        translate([0, 0, d + thickness_below_pcb + pcb_thickness])
            minkowski() {
                stitching_shape_base();
                cube(0.1);
            }
        stlink_drill();
        ethernet_drill();
    }
}

base_bottom();
//structure_rails_2d();

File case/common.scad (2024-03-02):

pcb_x = 92;
pcb_y = 138;
pcb_thickness = 1.55;
pcb_margin = 0.15;
thickness_below_pcb = 21.5;
support_nucleo_pins_h = 1.05;
structure_rails_height = 6.0;
d = 1.5;
m3_mount_diameter = 9.2;
m3_mount_h = 6; 
m3_drill_diameter = 2.8;
m3_passthrough_diameter = 3.2;
m3_head_h = 3.0;
m3_head_diameter = 5.8;
m3_long_length = 30.6; // M3x30 with additional margin

top_height = 14.5;
top_empty_height = 6.3;

motor_port_y = [24, 69, 114];
motor_width = 32.5;

m3_x = [5, 5, 46.98, 80.00];
m3_y = [5, 133, 80.86, 28.79];
$fn = 32;

corridor_x = 21.5;
corridor_y = 68.5;
corridor_w = 16;
corridor_len = 63.0;
corridor_horiz_y = 12.89;
dcdc_len = 25;
dcdc_w = 17;
dcdc_h = 9;

fan_d = 20.3;
fan_thickness = 10.7;
fan_height = 7.5;
fan_ribs_h_from_pcb = 27.5;
    
module stitching_shape_base() {
    square_d = sqrt(2) * pcb_thickness;
    union() {
        translate([10, -pcb_margin - d, 0])
            rotate(-90, [1, 0, 0])
                rotate(45, [0, 0, 1])
                    linear_extrude(d)
                        square(square_d, center=true);
        translate([10, pcb_y + pcb_margin, 0])
            rotate(-90, [1, 0, 0])
                rotate(45, [0, 0, 1])
                    linear_extrude(d)
                        square(square_d, center=true);
        translate([pcb_x + pcb_margin, 43, 0])
            rotate(90, [0, 1, 0])
                rotate(45, [0, 0, 1])
                    linear_extrude(d)
                        square(square_d, center=true);
        translate([-pcb_margin - d, motor_port_y[0] / 2 + motor_port_y[1] / 2, 0])
            rotate(90, [0, 1, 0])
                rotate(45, [0, 0, 1])
                    linear_extrude(d)
                        square(square_d, center=true);
        translate([-pcb_margin - d, motor_port_y[1] / 2 + motor_port_y[2] / 2, 0])
            rotate(90, [0, 1, 0])
                rotate(45, [0, 0, 1])
                    linear_extrude(d)
                        square(square_d, center=true);
    }
}

//stitching_shape_base();

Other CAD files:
case/top.scad

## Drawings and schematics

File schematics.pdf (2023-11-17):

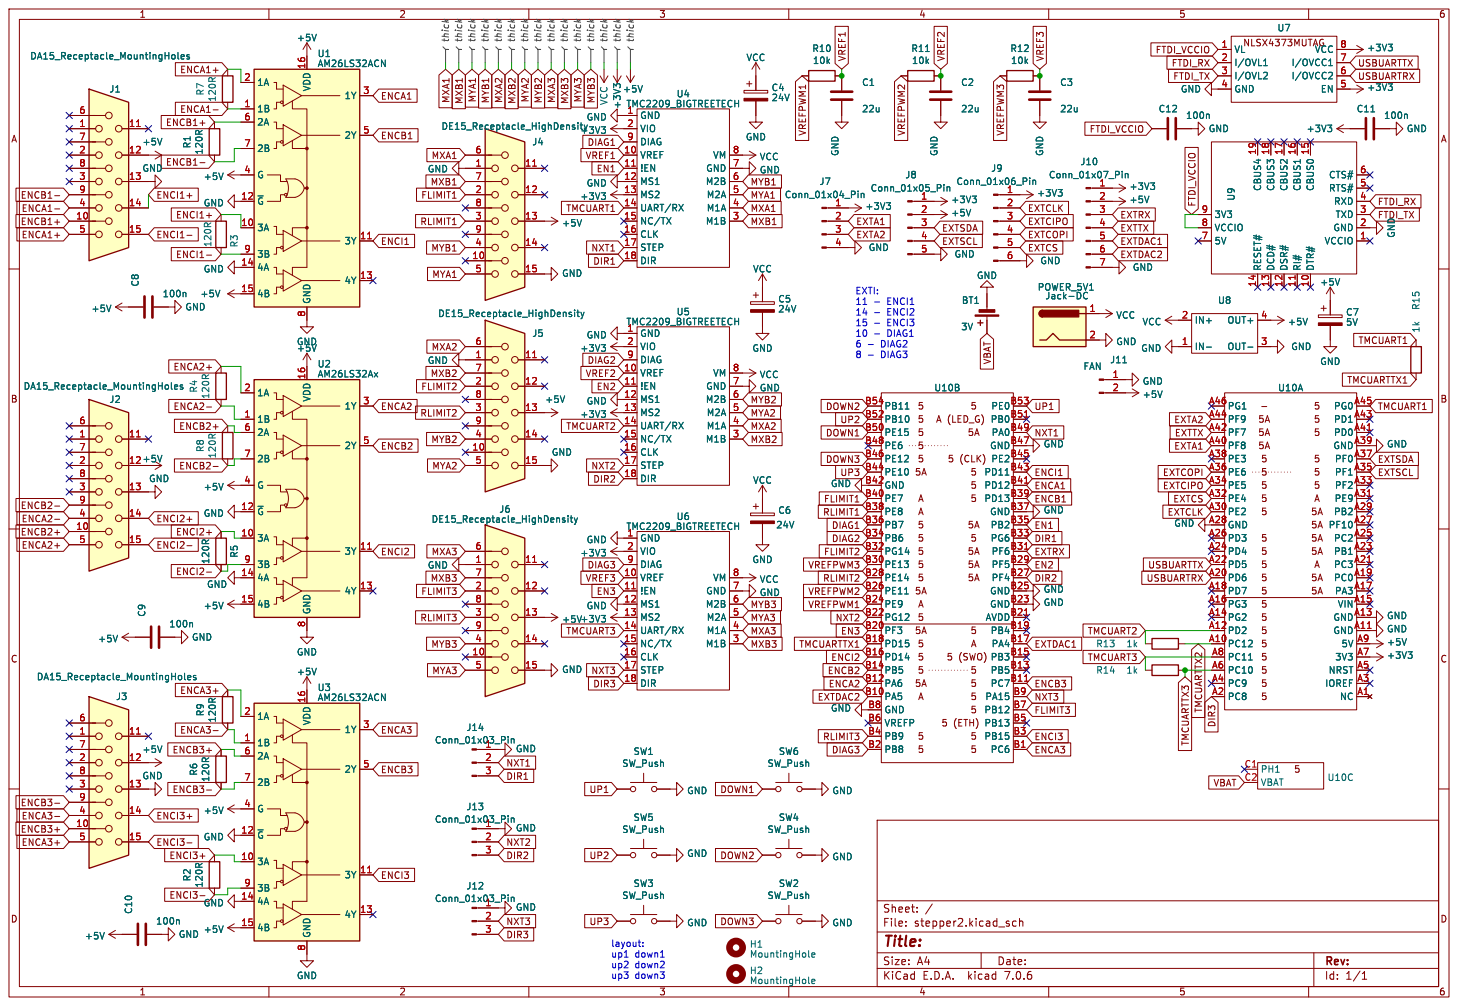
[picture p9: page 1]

Id: 1/1 Title: File: stepper2.kicad_sch Sheet: /

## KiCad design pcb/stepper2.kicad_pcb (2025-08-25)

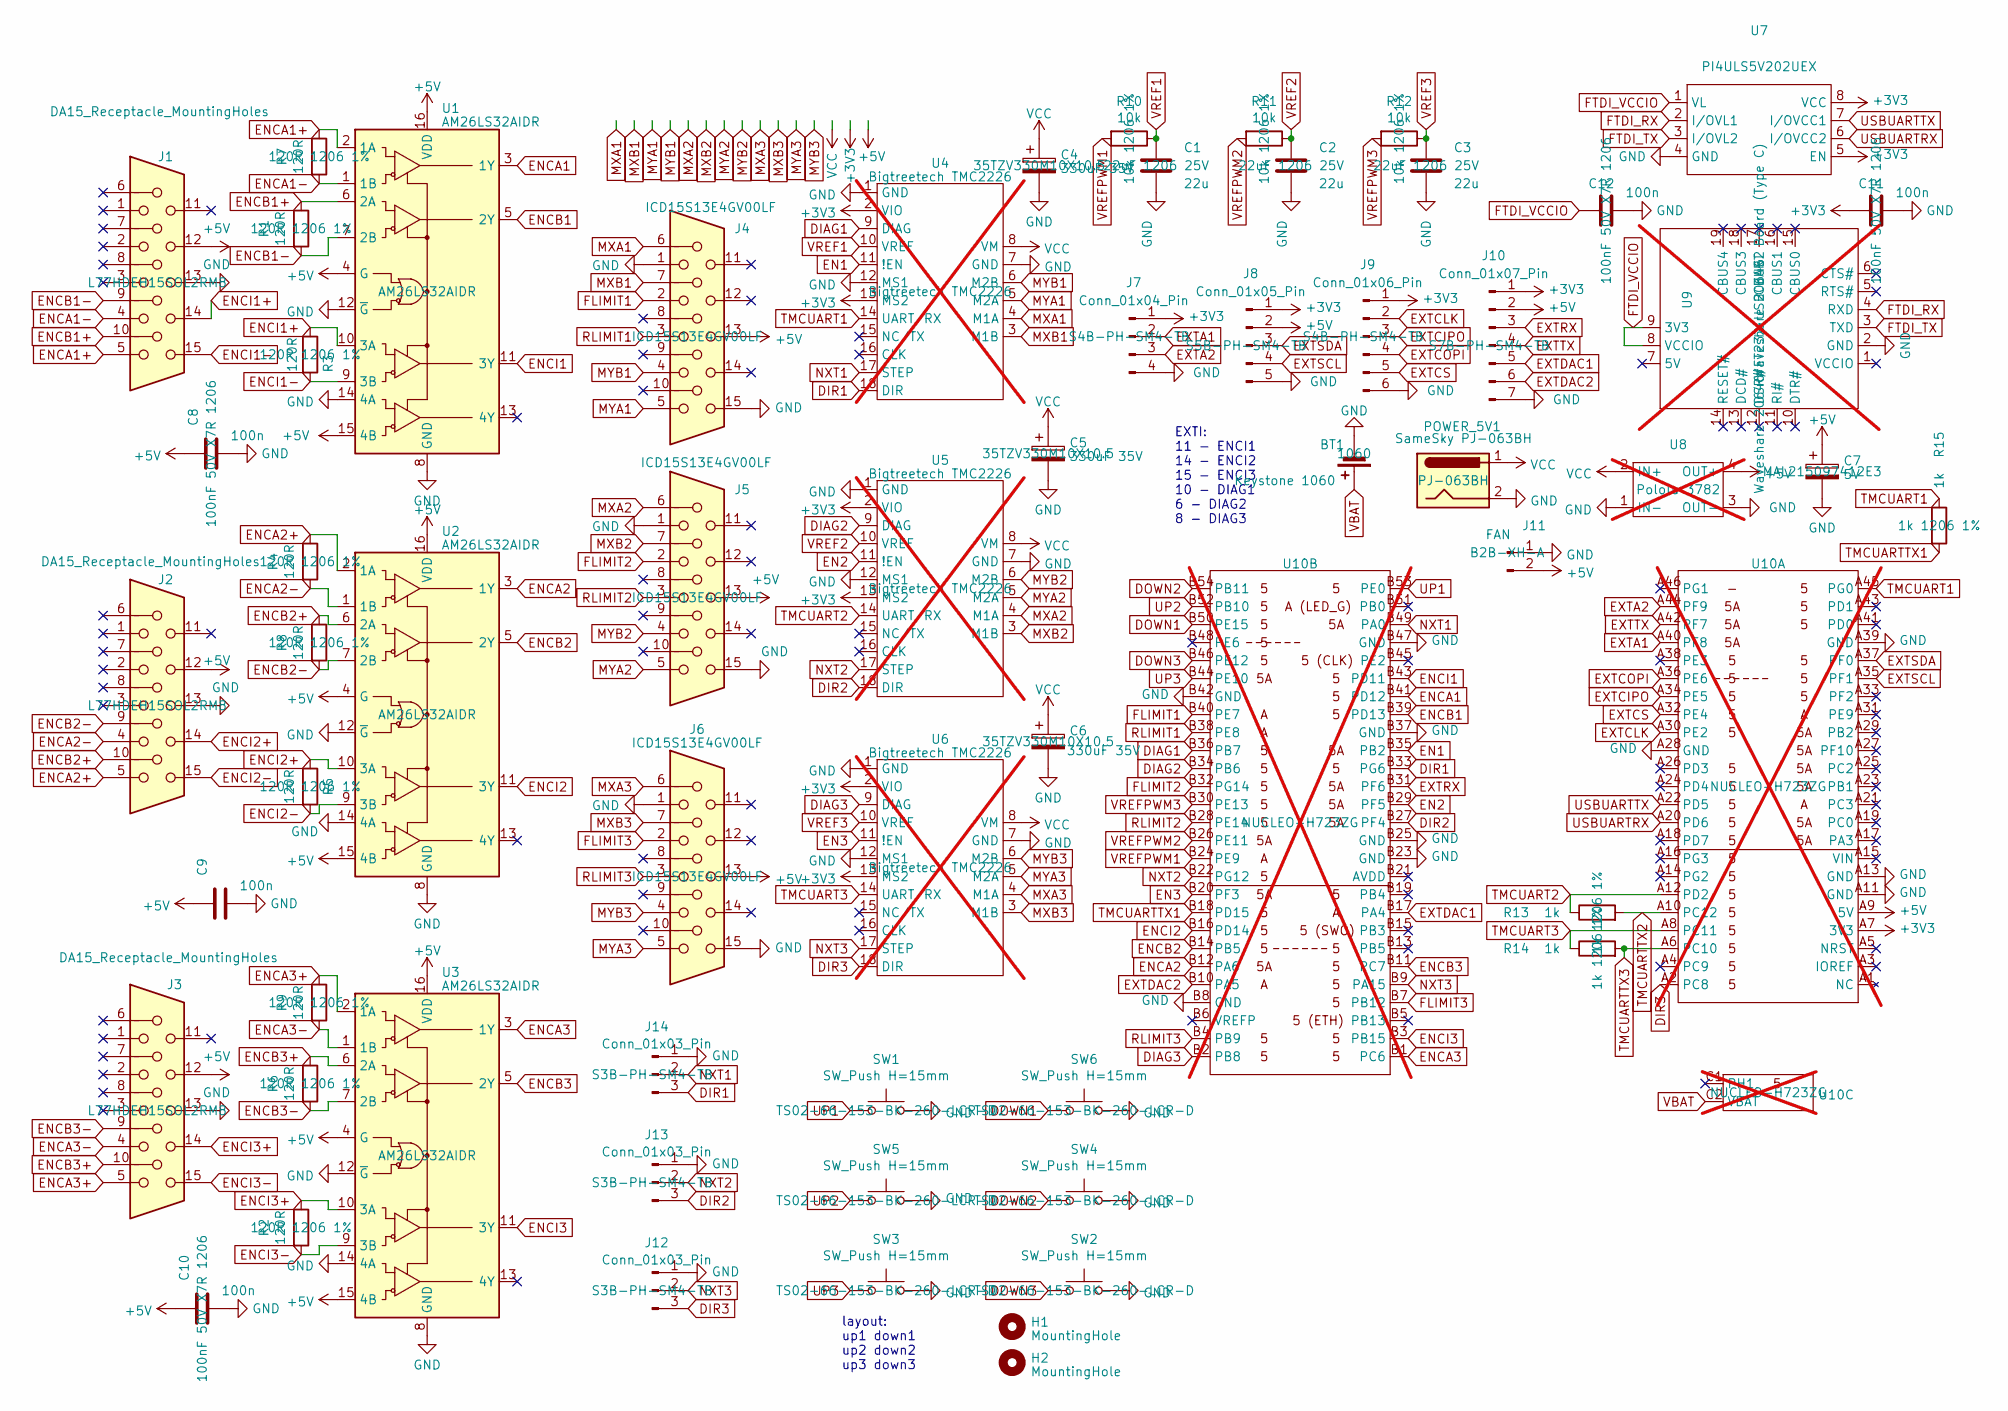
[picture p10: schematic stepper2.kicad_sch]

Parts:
BT1: Keystone 1060; BatteryHolder_Keystone_1060_1x2032; mpn 1060
C1, C2, C3: 22u; C_1206_3216Metric_Pad1.33x1.80mm_HandSolder; mpn 22uF 1206 25V; LCSC C12891
C4, C5, C6: 330uF 35V; CP_Elec_10x10.5; mpn 35TZV330M10X10.5; LCSC C2880403
C7: 5V; CP_Elec_8x10.5; mpn MAL215097412E3; LCSC C310836
C8, C9, C10, C11, C12: 100n; C_1206_3216Metric_Pad1.33x1.80mm_HandSolder; mpn 100nF 50V X7R 1206; LCSC C24497
H1, H2: MountingHole; MountingHole_3.2mm_M3
J1, J2, J3: DA15_Receptacle_MountingHoles; DSUB-15-HD_Vertical_Pitch2.29x1.98mm_Mercury3000_Enc; mpn L77HDEH15SOL2RM8
J4, J5, J6: ICD15S13E4GV00LF; DSUB-15-HD_Horizontal_Pitch2.29x2.54mm_EdgePinOffset9.40mm; mpn ICD15S13E4GV00LF
J7: Conn_01x04_Pin; JST_PH_S4B-PH-SM4-TB_1x04-1MP_P2.00mm_Horizontal; mpn S4B-PH-SM4-TB; LCSC C265102
J8: Conn_01x05_Pin; JST_PH_S5B-PH-SM4-TB_1x05-1MP_P2.00mm_Horizontal; mpn S5B-PH-SM4-TB; LCSC C265104
J9: Conn_01x06_Pin; JST_PH_S6B-PH-SM4-TB_1x06-1MP_P2.00mm_Horizontal; mpn S4B-PH-SM4-TB; LCSC C265405
J10: Conn_01x07_Pin; JST_PH_S7B-PH-SM4-TB_1x07-1MP_P2.00mm_Horizontal; mpn S7B-PH-SM4-TB; LCSC C265453
J11: FAN; JST_XH_B2B-XH-AM_1x02_P2.50mm_Vertical; mpn B2B-XH-A
J12, J13, J14: Conn_01x03_Pin; JST_PH_S3B-PH-SM4-TB_1x03-1MP_P2.00mm_Horizontal; mpn S3B-PH-SM4-TB; LCSC C265101
POWER_5V1: SameSky PJ-063BH; BarrelJack_CUI_PJ-063AH_Horizontal_CircularHoles; mpn PJ-063BH
R1, R2, R3, R4, R5, R6, R7, R8, R9: 120R; R_1206_3216Metric_Pad1.30x1.75mm_HandSolder; mpn 120R 1206 1%; LCSC C17909
R10, R11, R12: 10k; R_1206_3216Metric_Pad1.30x1.75mm_HandSolder; mpn 10k 1206 1%; LCSC C17902
R13, R14, R15: 1k; R_1206_3216Metric_Pad1.30x1.75mm_HandSolder; mpn 1k 1206 1%; LCSC C4410
SW1, SW2, SW3, SW4, SW5, SW6: SW_Push H=15mm; SW_PUSH_6mm_H4.3mm; mpn TS02-66-153-BK-260-LCR-D
U1, U2, U3: AM26LS32AIDR; SO-16_3.9x9.9mm_P1.27mm; mpn AM26LS32AIDR; LCSC C19092
U4, U5, U6: Bigtreetech TMC2226; TMC2209_BIGTREETECH; mpn Bigtreetech TMC2226; not fitted
U7: MSOP-8_3x3mm_P0.65mm; mpn PI4ULS5V202UEX; LCSC C481697
U8: POLOLU_3782; mpn Pololu 3782; not fitted
U9: Waveshare 20646 FT232 USB UART Board (Type C); Waveshare_FT232_USBC_module; mpn Waveshare 20646; not fitted
U10: Nucleo144_H723_withVBAT; mpn NUCLEO-H723ZG; not fitted

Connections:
+3V3: C11.1, J7.1, J8.1, J9.1, J10.1, U4.2 (VIO), U4.13 (MS2), U5.2 (VIO), U5.13 (MS2), U6.2 (VIO), U6.13 (MS2), U7.5 (EN), U7.8 (VCC), U10.A7 (3V3)
+5V: C7.1, C8.1, C9.1, C10.1, J1.12, J2.12, J3.12, J4.13, J5.13, J6.13, J8.2, J10.2, J11.2, U1.4 (G), U1.15 (4B), U1.16 (VDD), U2.4 (G), U2.15 (4B), U2.16 (VDD), U3.4 (G), U3.15 (4B), U3.16 (VDD), U8.4 (OUT+), U10.A9 (5V)
DIAG1: U4.9 (DIAG), U10.B36 (PB7)
DIAG2: U5.9 (DIAG), U10.B34 (PB6)
DIAG3: U6.9 (DIAG), U10.B2 (PB8)
DIR1: J14.3, U4.18 (DIR), U10.B33 (PG6)
DIR2: J13.3, U5.18 (DIR), U10.B27 (PF4)
DIR3: J12.3, U6.18 (DIR), U10.A2 (PC8)
DOWN1: SW6.1, U10.B50 (PE15)
DOWN2: SW4.1, U10.B54 (PB11)
DOWN3: SW2.1, U10.B46 (PE12)
EN1: U4.11 (!EN), U10.B35 (PB2)
EN2: U5.11 (!EN), U10.B29 (PF5)
EN3: U6.11 (!EN), U10.B20 (PF3)
ENCA1: U1.3 (1Y), U10.B41 (PD12)
ENCA1+: J1.5, R7.1, U1.2 (1A)
ENCA1-: J1.4, R7.2, U1.1 (1B)
ENCA2: U2.3 (1Y), U10.B12 (PA6)
ENCA2+: J2.5, R4.1, U2.2 (1A)
ENCA2-: J2.4, R4.2, U2.1 (1B)
ENCA3: U3.3 (1Y), U10.B1 (PC6)
ENCA3+: J3.5, R9.1, U3.2 (1A)
ENCA3-: J3.4, R9.2, U3.1 (1B)
ENCB1: U1.5 (2Y), U10.B39 (PD13)
ENCB1+: J1.10, R1.1, U1.6 (2A)
ENCB1-: J1.9, R1.2, U1.7 (2B)
ENCB2: U2.5 (2Y), U10.B14 (PB5)
ENCB2+: J2.10, R8.1, U2.6 (2A)
ENCB2-: J2.9, R8.2, U2.7 (2B)
ENCB3: U3.5 (2Y), U10.B11 (PC7)
ENCB3+: J3.10, R6.1, U3.6 (2A)
ENCB3-: J3.9, R6.2, U3.7 (2B)
ENCI1: U1.11 (3Y), U10.B43 (PD11)
ENCI1+: J1.14, R3.1, U1.10 (3A)
ENCI1-: J1.15, R3.2, U1.9 (3B)
ENCI2: U2.11 (3Y), U10.B16 (PD14)
ENCI2+: J2.14, R5.1, U2.10 (3A)
ENCI2-: J2.15, R5.2, U2.9 (3B)
ENCI3: U3.11 (3Y), U10.B3 (PB15)
ENCI3+: J3.14, R2.1, U3.10 (3A)
ENCI3-: J3.15, R2.2, U3.9 (3B)
EXTA1: J7.2, U10.A40 (PF8)
EXTA2: J7.3, U10.A44 (PF9)
EXTCIPO: J9.3, U10.A34 (PE5)
EXTCLK: J9.2, U10.A30 (PE2)
EXTCOPI: J9.4, U10.A36 (PE6)
EXTCS: J9.5, U10.A32 (PE4)
EXTDAC1: J10.5, U10.B17 (PA4)
EXTDAC2: J10.6, U10.B10 (PA5)
EXTRX: J10.3, U10.B31 (PF6)
EXTSCL: J8.4, U10.A35 (PF1)
EXTSDA: J8.3, U10.A37 (PF0)
EXTTX: J10.4, U10.A42 (PF7)
FLIMIT1: J4.2, U10.B40 (PE7)
FLIMIT2: J5.2, U10.B32 (PG14)
FLIMIT3: J6.2, U10.B7 (PB12)
FTDI_RX: U7.2 (I/OVL1), U9.4 (RXD)
FTDI_TX: U7.3 (I/OVL2), U9.3 (TXD)
FTDI_VCCIO: C12.1, U7.1 (VL), U9.8 (VCCIO), U9.9 (3V3)
GND: BT1.2 (-), C1.2, C2.2, C3.2, C4.2, C5.2, C6.2, C7.2, C8.2, C9.2, C10.2, C11.2, C12.2, J1.13, J2.13, J3.13, J4.1, J4.15, J5.1, J5.15, J6.1, J6.15, J7.4, J8.5, J9.6, J10.7, J11.1, J12.1, J13.1, J14.1, POWER_5V1.2, SW1.2, SW2.2, SW3.2, SW4.2, SW5.2, SW6.2, U1.8 (GND), U1.12 (~G), U1.14 (4A), U2.8 (GND), U2.12 (~G), U2.14 (4A), U3.8 (GND), U3.12 (~G), U3.14 (4A), U4.1 (GND), U4.7 (GND), U4.12 (MS1), U5.1 (GND), U5.7 (GND), U5.12 (MS1), U6.1 (GND), U6.7 (GND), U6.12 (MS1), U7.4 (GND), U8.1 (IN-), U8.3 (OUT-), U9.2 (GND), U10.A11 (GND), U10.A13 (GND), U10.A28 (GND), U10.A39 (GND), U10.B8 (GND), U10.B23 (GND), U10.B25 (GND), U10.B37 (GND), U10.B42 (GND), U10.B47 (GND)
MXA1: J4.6, U4.4 (M1A)
MXA2: J5.6, U5.4 (M1A)
MXA3: J6.6, U6.4 (M1A)
MXB1: J4.7, U4.3 (M1B)
MXB2: J5.7, U5.3 (M1B)
MXB3: J6.7, U6.3 (M1B)
MYA1: J4.5, U4.5 (M2A)
MYA2: J5.5, U5.5 (M2A)
MYA3: J6.5, U6.5 (M2A)
MYB1: J4.4, U4.6 (M2B)
MYB2: J5.4, U5.6 (M2B)
MYB3: J6.4, U6.6 (M2B)
NXT1: J14.2, U4.17 (STEP), U10.B49 (PA0)
NXT2: J13.2, U5.17 (STEP), U10.B22 (PG12)
NXT3: J12.2, U6.17 (STEP), U10.B9 (PA15)
RLIMIT1: J4.3, U10.B38 (PE8)
RLIMIT2: J5.3, U10.B28 (PE14)
RLIMIT3: J6.3, U10.B4 (PB9)
TMCUART1: R15.1, U4.14 (UART/RX), U10.A45 (PG0)
TMCUART2: R13.1, U5.14 (UART/RX), U10.A12 (PD2)
TMCUART3: R14.1, U6.14 (UART/RX), U10.A8 (PC11)
TMCUARTTX1: R15.2, U10.B18 (PD15)
TMCUARTTX2: R13.2, U10.A10 (PC12)
TMCUARTTX3: R14.2, U10.A6 (PC10)
UP1: SW1.1, U10.B53 (PE0)
UP2: SW5.1, U10.B52 (PB10)
UP3: SW3.1, U10.B44 (PE10)
USBUARTRX: U7.6 (I/OVCC2), U10.A20 (PD6)
USBUARTTX: U7.7 (I/OVCC1), U10.A22 (PD5)
VBAT: BT1.1 (+), U10.C2 (VBAT)
VCC: C4.1, C5.1, C6.1, POWER_5V1.1, U4.8 (VM), U5.8 (VM), U6.8 (VM), U8.2 (IN+)
VREF1: C1.1, R10.1, U4.10 (VREF)
VREF2: C2.1, R11.1, U5.10 (VREF)
VREF3: C3.1, R12.1, U6.10 (VREF)
VREFPWM1: R10.2, U10.B24 (PE9)
VREFPWM2: R11.2, U10.B26 (PE11)
VREFPWM3: R12.2, U10.B30 (PE13)

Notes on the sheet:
layout: up1 down1 up2 down2 up3 down3
EXTI: 11 - ENCI1 14 - ENCI2 15 - ENCI3 10 - DIAG1 6 - DIAG2 8 - DIAG3

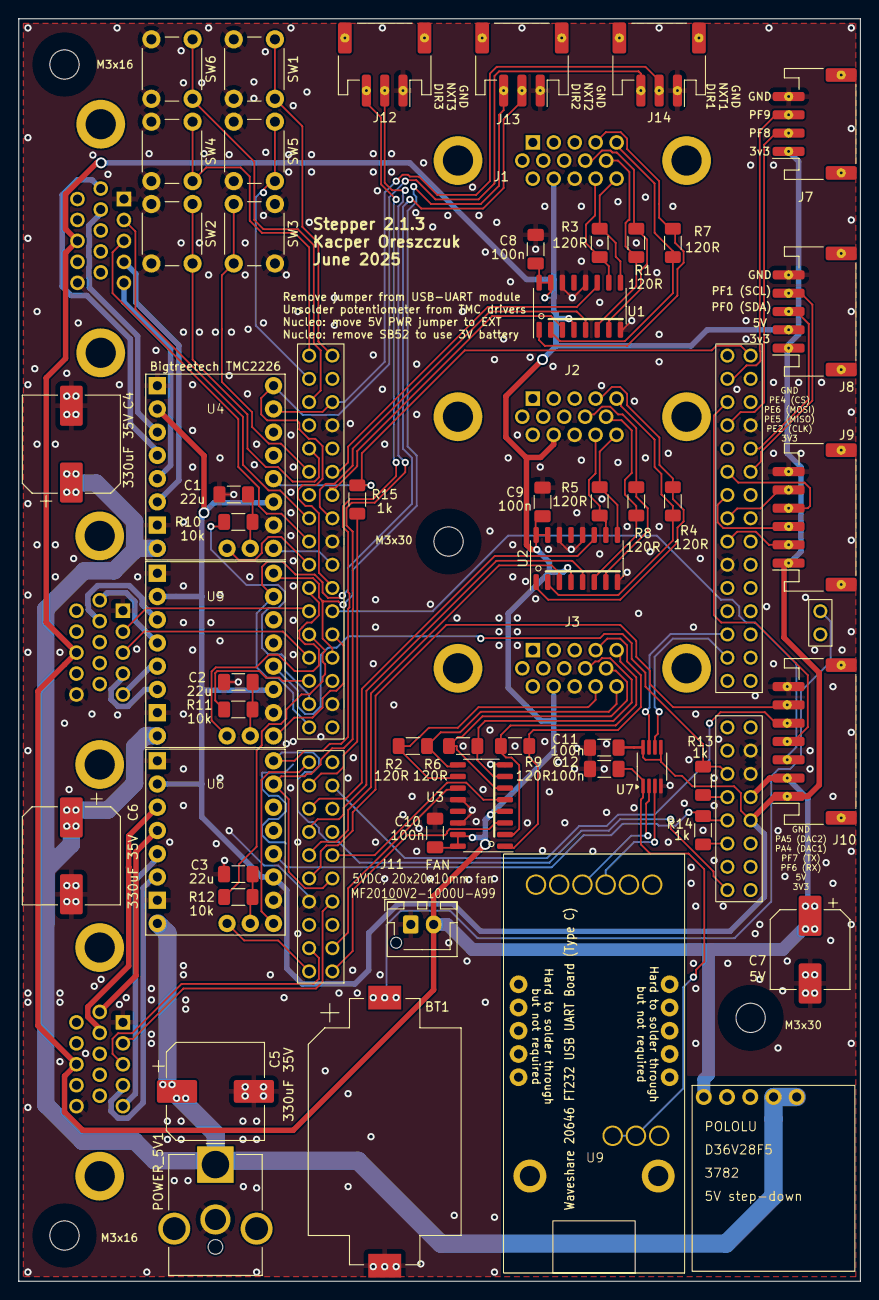
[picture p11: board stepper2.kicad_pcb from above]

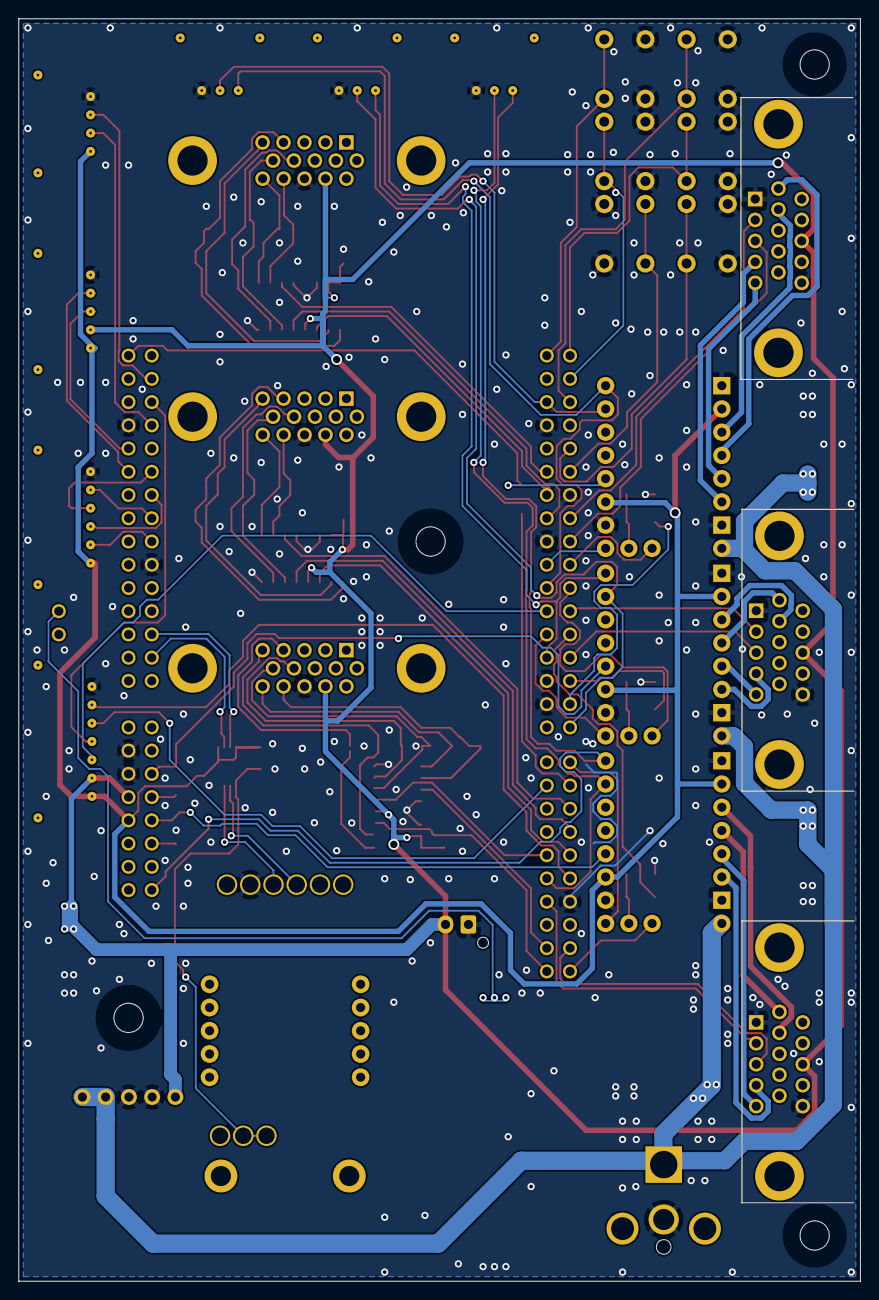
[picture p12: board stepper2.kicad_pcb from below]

Board: 2 copper layers, 92.0 x 138.0 mm, 61 parts (3 on the bottom side), 97 nets.

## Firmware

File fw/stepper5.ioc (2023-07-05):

#MicroXplorer Configuration settings - do not modify
CAD.formats=
CAD.pinconfig=
CAD.provider=
DAC1.DAC_Channel-DAC_OUT1=DAC_CHANNEL_1
DAC1.DAC_Channel-DAC_OUT2=DAC_CHANNEL_2
DAC1.IPParameters=DAC_Channel-DAC_OUT1,DAC_Channel-DAC_OUT2
ETH.IPParameters=MediaInterface
ETH.MediaInterface=HAL_ETH_RMII_MODE
File.Version=6
GPIO.groupedBy=
I2C5.IPParameters=Timing
I2C5.Timing=0x60404E72
KeepUserPlacement=false
Mcu.CPN=STM32H723ZGT6
Mcu.Family=STM32H7
Mcu.IP0=CORTEX_M7
Mcu.IP1=DAC1
Mcu.IP10=TIM2
Mcu.IP11=TIM3
Mcu.IP12=TIM4
Mcu.IP13=TIM5
Mcu.IP14=TIM8
Mcu.IP15=TIM23
Mcu.IP16=UART4
Mcu.IP17=UART5
Mcu.IP18=UART7
Mcu.IP19=UART9
Mcu.IP2=DEBUG
Mcu.IP20=USART2
Mcu.IP21=USART3
Mcu.IP22=USB_OTG_HS
Mcu.IP3=ETH
Mcu.IP4=I2C5
Mcu.IP5=NVIC
Mcu.IP6=RCC
Mcu.IP7=SPI4
Mcu.IP8=SYS
Mcu.IP9=TIM1
Mcu.IPNb=23
Mcu.Name=STM32H723ZGTx
Mcu.Package=LQFP144
Mcu.Pin0=PE2
Mcu.Pin1=PE4
Mcu.Pin10=PF4
Mcu.Pin11=PF5
Mcu.Pin12=PF6
Mcu.Pin13=PF7
Mcu.Pin14=PF8
Mcu.Pin15=PF9
Mcu.Pin16=PH0-OSC_IN
Mcu.Pin17=PH1-OSC_OUT
Mcu.Pin18=PC1
Mcu.Pin19=PA0
Mcu.Pin2=PE5
Mcu.Pin20=PA1
Mcu.Pin21=PA2
Mcu.Pin22=PA4
Mcu.Pin23=PA5
Mcu.Pin24=PA6
Mcu.Pin25=PA7
Mcu.Pin26=PC4
Mcu.Pin27=PC5
Mcu.Pin28=PB0
Mcu.Pin29=PB2
Mcu.Pin3=PE6
Mcu.Pin30=PG0
Mcu.Pin31=PE7
Mcu.Pin32=PE8
Mcu.Pin33=PE9
Mcu.Pin34=PE10
Mcu.Pin35=PE11
Mcu.Pin36=PE12
Mcu.Pin37=PE13
Mcu.Pin38=PE14
Mcu.Pin39=PE15
Mcu.Pin4=PC13
Mcu.Pin40=PB10
Mcu.Pin41=PB11
Mcu.Pin42=PB12
Mcu.Pin43=PB13
Mcu.Pin44=PB14
Mcu.Pin45=PB15
Mcu.Pin46=PD8
Mcu.Pin47=PD9
Mcu.Pin48=PD10
Mcu.Pin49=PD12
Mcu.Pin5=PC14-OSC32_IN
Mcu.Pin50=PD13
Mcu.Pin51=PD14
Mcu.Pin52=PD15
Mcu.Pin53=PG6
Mcu.Pin54=PC6
Mcu.Pin55=PC7
Mcu.Pin56=PC8
Mcu.Pin57=PA9
Mcu.Pin58=PA10
Mcu.Pin59=PA11
Mcu.Pin6=PC15-OSC32_OUT
Mcu.Pin60=PA12
Mcu.Pin61=PA13(JTMS/SWDIO)
Mcu.Pin62=PA14(JTCK/SWCLK)
Mcu.Pin63=PA15(JTDI)
Mcu.Pin64=PC10
Mcu.Pin65=PC11
Mcu.Pin66=PC12
Mcu.Pin67=PD2
Mcu.Pin68=PD5
Mcu.Pin69=PD6
Mcu.Pin7=PF0
Mcu.Pin70=PG11
Mcu.Pin71=PG12
Mcu.Pin72=PG13
Mcu.Pin73=PG14
Mcu.Pin74=PB3(JTDO/TRACESWO)
Mcu.Pin75=PB5
Mcu.Pin76=PB6
Mcu.Pin77=PB7
Mcu.Pin78=PB8
Mcu.Pin79=PB9
Mcu.Pin8=PF1
Mcu.Pin80=PE0
Mcu.Pin81=PE1
Mcu.Pin82=VP_SYS_VS_Systick
Mcu.Pin9=PF3
Mcu.PinsNb=83
Mcu.ThirdPartyNb=0
Mcu.UserConstants=
Mcu.UserName=STM32H723ZGTx
MxCube.Version=6.8.0
MxDb.Version=DB.6.0.80
NVIC.BusFault_IRQn=true\:0\:0\:false\:false\:true\:false\:false\:false
NVIC.DebugMonitor_IRQn=true\:0\:0\:false\:false\:true\:false\:false\:false
NVIC.ForceEnableDMAVector=true
NVIC.HardFault_IRQn=true\:0\:0\:false\:false\:true\:false\:false\:false
NVIC.MemoryManagement_IRQn=true\:0\:0\:false\:false\:true\:false\:false\:false
NVIC.NonMaskableInt_IRQn=true\:0\:0\:false\:false\:true\:false\:false\:false
NVIC.PendSV_IRQn=true\:0\:0\:false\:false\:true\:false\:false\:false
NVIC.PriorityGroup=NVIC_PRIORITYGROUP_4
NVIC.SVCall_IRQn=true\:0\:0\:false\:false\:true\:false\:false\:false
NVIC.SysTick_IRQn=true\:0\:0\:false\:false\:true\:false\:true\:false
NVIC.UsageFault_IRQn=true\:0\:0\:false\:false\:true\:false\:false\:false
PA0.GPIOParameters=GPIO_Label
PA0.GPIO_Label=NXT1
PA0.Signal=S_TIM5_CH1
PA1.GPIOParameters=GPIO_Label
PA1.GPIO_Label=RMII_REF_CLK
PA1.Locked=true
PA1.Mode=RMII
PA1.Signal=ETH_REF_CLK
PA10.GPIOParameters=GPIO_Label
PA10.GPIO_Label=USB_FS_ID
PA10.Locked=true
PA10.Mode=OTG/Dual-Role-Device-FS
PA10.Signal=USB_OTG_HS_ID
PA11.GPIOParameters=GPIO_Label
PA11.GPIO_Label=USB_FS_DM
PA11.Mode=OTG/Dual-Role-Device-FS
PA11.Signal=USB_OTG_HS_DM
PA12.GPIOParameters=GPIO_Label
PA12.GPIO_Label=USB_FS_DP
PA12.Mode=OTG/Dual-Role-Device-FS
PA12.Signal=USB_OTG_HS_DP
PA13(JTMS/SWDIO).GPIOParameters=GPIO_Label
PA13(JTMS/SWDIO).GPIO_Label=SWDIO
PA13(JTMS/SWDIO).Locked=true
PA13(JTMS/SWDIO).Mode=Trace_Asynchronous_SW
PA13(JTMS/SWDIO).Signal=DEBUG_JTMS-SWDIO
PA14(JTCK/SWCLK).GPIOParameters=GPIO_Label
PA14(JTCK/SWCLK).GPIO_Label=SWCLK
PA14(JTCK/SWCLK).Locked=true
PA14(JTCK/SWCLK).Mode=Trace_Asynchronous_SW
PA14(JTCK/SWCLK).Signal=DEBUG_JTCK-SWCLK
PA15(JTDI).GPIOParameters=GPIO_Label
PA15(JTDI).GPIO_Label=NXT3
PA15(JTDI).Signal=S_TIM2_CH1_ETR
PA2.GPIOParameters=GPIO_Label
PA2.GPIO_Label=RMII_MDIO
PA2.Locked=true
PA2.Mode=RMII
PA2.Signal=ETH_MDIO
PA4.GPIOParameters=GPIO_Label
PA4.GPIO_Label=EXTDAC1
PA4.Signal=COMP_DAC11_group
PA5.GPIOParameters=GPIO_Label
PA5.GPIO_Label=EXTDAC2
PA5.Signal=COMP_DAC12_group
PA6.GPIOParameters=GPIO_Label
PA6.GPIO_Label=ENCA2
PA6.Signal=S_TIM3_CH1
PA7.GPIOParameters=GPIO_Label
PA7.GPIO_Label=RMII_CRS_DV
PA7.Locked=true
PA7.Mode=RMII
PA7.Signal=ETH_CRS_DV
PA9.GPIOParameters=GPIO_Label
PA9.GPIO_Label=USB_FS_VBUS
PA9.Locked=true
PA9.Mode=Activate_VBUS_FS
PA9.Signal=USB_OTG_HS_VBUS
PB0.GPIOParameters=GPIO_Label
PB0.GPIO_Label=LED_GREEN
PB0.Locked=true
PB0.Signal=GPIO_Output
PB10.GPIOParameters=GPIO_Label
PB10.GPIO_Label=DOWN2
PB10.Locked=true
PB10.Signal=GPIO_Input
PB11.GPIOParameters=GPIO_Label
PB11.GPIO_Label=DOWN1
PB11.Locked=true
PB11.Signal=GPIO_Input
PB12.GPIOParameters=GPIO_Label
PB12.GPIO_Label=FLIMIT3
PB12.Locked=true
PB12.Signal=GPIO_Input
PB13.GPIOParameters=GPIO_Label
PB13.GPIO_Label=RMII_TXD1
PB13.Locked=true
PB13.Mode=RMII
PB13.Signal=ETH_TXD1
PB14.GPIOParameters=GPIO_Label
PB14.GPIO_Label=LED_RED
PB14.Locked=true
PB14.Signal=GPIO_Output
PB15.GPIOParameters=GPIO_Label
PB15.GPIO_Label=ENCI3
PB15.Locked=true
PB15.Signal=GPXTI15
PB2.GPIOParameters=GPIO_Label
PB2.GPIO_Label=EN1
PB2.Locked=true
PB2.Signal=GPIO_Output
PB3(JTDO/TRACESWO).GPIOParameters=GPIO_Label
PB3(JTDO/TRACESWO).GPIO_Label=SWO
PB3(JTDO/TRACESWO).Locked=true
PB3(JTDO/TRACESWO).Mode=Trace_Asynchronous_SW
PB3(JTDO/TRACESWO).Signal=DEBUG_JTDO-SWO
PB5.GPIOParameters=GPIO_Label
PB5.GPIO_Label=ENCB2
PB5.Signal=S_TIM3_CH2
PB6.GPIOParameters=GPIO_Label
PB6.GPIO_Label=DIAG2
PB6.Locked=true
PB6.Signal=GPXTI6
PB7.GPIOParameters=GPIO_Label
PB7.GPIO_Label=DIAG1
PB7.Locked=true
PB7.Signal=GPXTI7
PB8.GPIOParameters=GPIO_Label
PB8.GPIO_Label=DIAG3
PB8.Locked=true
PB8.Signal=GPXTI8
PB9.GPIOParameters=GPIO_Label
PB9.GPIO_Label=RLIMIT3
PB9.Locked=true
PB9.Signal=GPIO_Input
PC1.GPIOParameters=GPIO_Label
PC1.GPIO_Label=RMII_MDC
PC1.Locked=true
PC1.Mode=RMII
PC1.Signal=ETH_MDC
PC10.GPIOParameters=GPIO_Label
PC10.GPIO_Label=TMCUARTTX3
PC10.Locked=true
PC10.Mode=Asynchronous
PC10.Signal=UART4_TX
PC11.GPIOParameters=GPIO_Label
PC11.GPIO_Label=TMCUARTRX3
PC11.Mode=Asynchronous
PC11.Signal=UART4_RX
PC12.GPIOParameters=GPIO_Label
PC12.GPIO_Label=TMCUARTTX2
PC12.Mode=Asynchronous
PC12.Signal=UART5_TX
PC13.GPIOParameters=GPIO_Label
PC13.GPIO_Label=B1 (Blue_User_Button)
PC13.Locked=true
PC13.Signal=GPIO_Input
PC14-OSC32_IN.Locked=true
PC14-OSC32_IN.Mode=LSE-External-Oscillator
PC14-OSC32_IN.Signal=RCC_OSC32_IN
PC15-OSC32_OUT.Locked=true
PC15-OSC32_OUT.Mode=LSE-External-Oscillator
PC15-OSC32_OUT.Signal=RCC_OSC32_OUT
PC4.GPIOParameters=GPIO_Label
PC4.GPIO_Label=RMII_RXD0
PC4.Locked=true
PC4.Mode=RMII
PC4.Signal=ETH_RXD0
PC5.GPIOParameters=GPIO_Label
PC5.GPIO_Label=RMII_RXD1
PC5.Locked=true
PC5.Mode=RMII
PC5.Signal=ETH_RXD1
PC6.GPIOParameters=GPIO_Label
PC6.GPIO_Label=ENCA3
PC6.Signal=S_TIM8_CH1
PC7.GPIOParameters=GPIO_Label
PC7.GPIO_Label=ENCB3
PC7.Signal=S_TIM8_CH2
PC8.GPIOParameters=GPIO_Label
PC8.GPIO_Label=DIR3
PC8.Locked=true
PC8.Signal=GPIO_Output
PD10.Locked=true
PD10.Signal=GPIO_Output
PD12.GPIOParameters=GPIO_Label
PD12.GPIO_Label=ENCA1
PD12.Signal=S_TIM4_CH1
PD13.GPIOParameters=GPIO_Label
PD13.GPIO_Label=ENCB1
PD13.Signal=S_TIM4_CH2
PD14.GPIOParameters=GPIO_Label
PD14.GPIO_Label=ENCI2
PD14.Locked=true
PD14.Signal=GPXTI14
PD15.GPIOParameters=GPIO_Label
PD15.GPIO_Label=TMCUARTTX1
PD15.Locked=true
PD15.Mode=Asynchronous
PD15.Signal=UART9_TX
PD2.GPIOParameters=GPIO_Label
PD2.GPIO_Label=TMCUARTRX2
PD2.Locked=true
PD2.Mode=Asynchronous
PD2.Signal=UART5_RX
PD5.GPIOParameters=GPIO_Label
PD5.GPIO_Label=USBUARTTX
PD5.Mode=Asynchronous
PD5.Signal=USART2_TX
PD6.GPIOParameters=GPIO_Label
PD6.GPIO_Label=USBUARTRX
PD6.Locked=true
PD6.Mode=Asynchronous
PD6.Signal=USART2_RX
PD8.GPIOParameters=GPIO_Label
PD8.GPIO_Label=STLK_VCP_RX
PD8.Locked=true
PD8.Mode=Asynchronous
PD8.Signal=USART3_TX
PD9.GPIOParameters=GPIO_Label
PD9.GPIO_Label=STLK_VCP_TX
PD9.Locked=true
PD9.Mode=Asynchronous
PD9.Signal=USART3_RX
PE0.GPIOParameters=GPIO_Label
PE0.GPIO_Label=UP1
PE0.Locked=true
PE0.Signal=GPIO_Input
PE1.GPIOParameters=GPIO_Label
PE1.GPIO_Label=LED_YELLOW
PE1.Locked=true
PE1.Signal=GPIO_Output
PE10.GPIOParameters=GPIO_Label
PE10.GPIO_Label=UP3
PE10.Locked=true
PE10.Signal=GPIO_Input
PE11.GPIOParameters=GPIO_Label
PE11.GPIO_Label=VREFPWM2
PE11.Signal=S_TIM1_CH2
PE12.GPIOParameters=GPIO_Label
PE12.GPIO_Label=UP2
PE12.Locked=true
PE12.Signal=GPIO_Input
PE13.GPIOParameters=GPIO_Label
PE13.GPIO_Label=VREFPWM3
PE13.Signal=S_TIM1_CH3
PE14.GPIOParameters=GPIO_Label
PE14.GPIO_Label=RLIMIT2
PE14.Locked=true
PE14.Signal=GPIO_Input
PE15.GPIOParameters=GPIO_Label
PE15.GPIO_Label=DOWN3
PE15.Locked=true
PE15.Signal=GPIO_Input
PE2.GPIOParameters=GPIO_Label
PE2.GPIO_Label=EXTCLK
PE2.Locked=true
PE2.Mode=Full_Duplex_Master
PE2.Signal=SPI4_SCK
PE4.GPIOParameters=GPIO_Label
PE4.GPIO_Label=EXTCS
PE4.Mode=NSS_Signal_Hard_Output
PE4.Signal=SPI4_NSS
PE5.GPIOParameters=GPIO_Label
PE5.GPIO_Label=EXTCIPO
PE5.Mode=Full_Duplex_Master
PE5.Signal=SPI4_MISO
PE6.GPIOParameters=GPIO_Label
PE6.GPIO_Label=EXTCOPI
PE6.Mode=Full_Duplex_Master
PE6.Signal=SPI4_MOSI
PE7.GPIOParameters=GPIO_Label
PE7.GPIO_Label=FLIMIT1
PE7.Locked=true
PE7.Signal=GPIO_Input
PE8.GPIOParameters=GPIO_Label
PE8.GPIO_Label=RLIMIT1
PE8.Locked=true
PE8.Signal=GPIO_Input
PE9.GPIOParameters=GPIO_Label
PE9.GPIO_Label=VREFPWM1
PE9.Signal=S_TIM1_CH1
PF0.GPIOParameters=GPIO_Label
PF0.GPIO_Label=EXTSDA
PF0.Mode=I2C
PF0.Signal=I2C5_SDA
PF1.GPIOParameters=GPIO_Label
PF1.GPIO_Label=EXTSCL
PF1.Mode=I2C
PF1.Signal=I2C5_SCL
PF3.GPIOParameters=GPIO_Label
PF3.GPIO_Label=EN3
PF3.Locked=true
PF3.Signal=GPIO_Output
PF4.GPIOParameters=GPIO_Label
PF4.GPIO_Label=DIR2
PF4.Locked=true
PF4.Signal=GPIO_Output
PF5.GPIOParameters=GPIO_Label
PF5.GPIO_Label=EN2
PF5.Locked=true
PF5.Signal=GPIO_Output
PF6.GPIOParameters=GPIO_Label
PF6.GPIO_Label=EXTRXUART
PF6.Locked=true
PF6.Mode=Asynchronous
PF6.Signal=UART7_RX
PF7.GPIOParameters=GPIO_Label
PF7.GPIO_Label=EXTTXUART
PF7.Locked=true
PF7.Mode=Asynchronous
PF7.Signal=UART7_TX
PF8.GPIOParameters=GPIO_Label
PF8.GPIO_Label=EXTA1
PF8.Locked=true
PF8.Signal=GPIO_Analog
PF9.GPIOParameters=GPIO_Label
PF9.GPIO_Label=EXTA2
PF9.Locked=true
PF9.Signal=GPIO_Analog
PG0.GPIOParameters=GPIO_Label
PG0.GPIO_Label=TMCUARTRX1
PG0.Mode=Asynchronous
PG0.Signal=UART9_RX
PG11.GPIOParameters=GPIO_Label
PG11.GPIO_Label=RMII_TX_EN
PG11.Locked=true
PG11.Mode=RMII
PG11.Signal=ETH_TX_EN
PG12.GPIOParameters=GPIO_Label
PG12.GPIO_Label=NXT2
PG12.Locked=true
PG12.Mode=PWM Generation1 CH1
PG12.Signal=TIM23_CH1
PG13.GPIOParameters=GPIO_Label
PG13.GPIO_Label=RMII_TXD0
PG13.Locked=true
PG13.Mode=RMII
PG13.Signal=ETH_TXD0
PG14.GPIOParameters=GPIO_Label
PG14.GPIO_Label=FLIMIT2
PG14.Locked=true
PG14.Signal=GPIO_Input
PG6.GPIOParameters=GPIO_Label
PG6.GPIO_Label=DIR1
PG6.Locked=true
PG6.Signal=GPIO_Output
PH0-OSC_IN.GPIOParameters=GPIO_Label
PH0-OSC_IN.GPIO_Label=MCO
PH0-OSC_IN.Locked=true
PH0-OSC_IN.Mode=HSE-External-Clock-Source
PH0-OSC_IN.Signal=RCC_OSC_IN
PH1-OSC_OUT.Locked=true
PH1-OSC_OUT.Signal=RCC_OSC_OUT
PinOutPanel.RotationAngle=0
ProjectManager.AskForMigrate=true
ProjectManager.BackupPrevious=false
ProjectManager.CompilerOptimize=6
ProjectManager.ComputerToolchain=false
ProjectManager.CoupleFile=false
ProjectManager.CustomerFirmwarePackage=
ProjectManager.DefaultFWLocation=true
ProjectManager.DeletePrevious=true
ProjectManager.DeviceId=STM32H723ZGTx
ProjectManager.FirmwarePackage=STM32Cube FW_H7 V1.11.0
ProjectManager.FreePins=false
ProjectManager.HalAssertFull=false
ProjectManager.HeapSize=0x200
ProjectManager.KeepUserCode=true
ProjectManager.LastFirmware=true
ProjectManager.LibraryCopy=1
ProjectManager.MainLocation=Core/Src
ProjectManager.NoMain=false
ProjectManager.PreviousToolchain=
ProjectManager.ProjectBuild=false
ProjectManager.ProjectFileName=stepper5.ioc
ProjectManager.ProjectName=stepper5
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

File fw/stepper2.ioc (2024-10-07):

#MicroXplorer Configuration settings - do not modify
CAD.formats=
CAD.pinconfig=
CAD.provider=
DAC1.DAC_Channel-DAC_OUT1=DAC_CHANNEL_1
DAC1.DAC_Channel-DAC_OUT2=DAC_CHANNEL_2
DAC1.IPParameters=DAC_Channel-DAC_OUT1,DAC_Channel-DAC_OUT2
Dma.Request0=USART2_RX
Dma.Request1=UART9_RX
Dma.Request2=UART5_RX
Dma.Request3=UART4_RX
Dma.RequestsNb=4
Dma.UART4_RX.3.Direction=DMA_PERIPH_TO_MEMORY
Dma.UART4_RX.3.EventEnable=DISABLE
Dma.UART4_RX.3.FIFOMode=DMA_FIFOMODE_DISABLE
Dma.UART4_RX.3.Instance=DMA1_Stream3
Dma.UART4_RX.3.MemDataAlignment=DMA_MDATAALIGN_BYTE
Dma.UART4_RX.3.MemInc=DMA_MINC_ENABLE
Dma.UART4_RX.3.Mode=DMA_CIRCULAR
Dma.UART4_RX.3.PeriphDataAlignment=DMA_PDATAALIGN_BYTE
Dma.UART4_RX.3.PeriphInc=DMA_PINC_DISABLE
Dma.UART4_RX.3.Polarity=HAL_DMAMUX_REQ_GEN_RISING
Dma.UART4_RX.3.Priority=DMA_PRIORITY_LOW
Dma.UART4_RX.3.RequestNumber=1
Dma.UART4_RX.3.RequestParameters=Instance,Direction,PeriphInc,MemInc,PeriphDataAlignment,MemDataAlignment,Mode,Priority,FIFOMode,SignalID,Polarity,RequestNumber,SyncSignalID,SyncPolarity,SyncEnable,EventEnable,SyncRequestNumber
Dma.UART4_RX.3.SignalID=NONE
Dma.UART4_RX.3.SyncEnable=DISABLE
Dma.UART4_RX.3.SyncPolarity=HAL_DMAMUX_SYNC_NO_EVENT
Dma.UART4_RX.3.SyncRequestNumber=1
Dma.UART4_RX.3.SyncSignalID=NONE
Dma.UART5_RX.2.Direction=DMA_PERIPH_TO_MEMORY
Dma.UART5_RX.2.EventEnable=DISABLE
Dma.UART5_RX.2.FIFOMode=DMA_FIFOMODE_DISABLE
Dma.UART5_RX.2.Instance=DMA1_Stream2
Dma.UART5_RX.2.MemDataAlignment=DMA_MDATAALIGN_BYTE
Dma.UART5_RX.2.MemInc=DMA_MINC_ENABLE
Dma.UART5_RX.2.Mode=DMA_CIRCULAR
Dma.UART5_RX.2.PeriphDataAlignment=DMA_PDATAALIGN_BYTE
Dma.UART5_RX.2.PeriphInc=DMA_PINC_DISABLE
Dma.UART5_RX.2.Polarity=HAL_DMAMUX_REQ_GEN_RISING
Dma.UART5_RX.2.Priority=DMA_PRIORITY_LOW
Dma.UART5_RX.2.RequestNumber=1
Dma.UART5_RX.2.RequestParameters=Instance,Direction,PeriphInc,MemInc,PeriphDataAlignment,MemDataAlignment,Mode,Priority,FIFOMode,SignalID,Polarity,RequestNumber,SyncSignalID,SyncPolarity,SyncEnable,EventEnable,SyncRequestNumber
Dma.UART5_RX.2.SignalID=NONE
Dma.UART5_RX.2.SyncEnable=DISABLE
Dma.UART5_RX.2.SyncPolarity=HAL_DMAMUX_SYNC_NO_EVENT
Dma.UART5_RX.2.SyncRequestNumber=1
Dma.UART5_RX.2.SyncSignalID=NONE
Dma.UART9_RX.1.Direction=DMA_PERIPH_TO_MEMORY
Dma.UART9_RX.1.EventEnable=DISABLE
Dma.UART9_RX.1.FIFOMode=DMA_FIFOMODE_DISABLE
Dma.UART9_RX.1.Instance=DMA1_Stream1
Dma.UART9_RX.1.MemDataAlignment=DMA_MDATAALIGN_BYTE
Dma.UART9_RX.1.MemInc=DMA_MINC_ENABLE
Dma.UART9_RX.1.Mode=DMA_CIRCULAR
Dma.UART9_RX.1.PeriphDataAlignment=DMA_PDATAALIGN_BYTE
Dma.UART9_RX.1.PeriphInc=DMA_PINC_DISABLE
Dma.UART9_RX.1.Polarity=HAL_DMAMUX_REQ_GEN_RISING
Dma.UART9_RX.1.Priority=DMA_PRIORITY_LOW
Dma.UART9_RX.1.RequestNumber=1
Dma.UART9_RX.1.RequestParameters=Instance,Direction,PeriphInc,MemInc,PeriphDataAlignment,MemDataAlignment,Mode,Priority,FIFOMode,SignalID,Polarity,RequestNumber,SyncSignalID,SyncPolarity,SyncEnable,EventEnable,SyncRequestNumber
Dma.UART9_RX.1.SignalID=NONE
Dma.UART9_RX.1.SyncEnable=DISABLE
Dma.UART9_RX.1.SyncPolarity=HAL_DMAMUX_SYNC_NO_EVENT
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

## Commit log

2023-05-24 Init commit - scetch of the PCB and empty firmware project
    [stepper2.kicad_pcb, stepper2.kicad_sch]
2023-05-24 footprints for serial USB converter and DCDC module
    [stepper2.kicad_pcb, stepper2.kicad_sch]
2023-05-25 Nucleo footprint and updates on schematics
    [stepper2.kicad_pcb, stepper2.kicad_sch]
2023-05-26 Basic layout of the PCB, encoder connectors added
    [stepper2.kicad_pcb, stepper2.kicad_sch]
2023-06-12 partial pin mapping in schematics and cube project
    [stepper2.kicad_sch]
2023-06-13 more connections added to schematic
    [stepper2.kicad_sch]
2023-06-21 labels on buttons on schematics
    [stepper2.kicad_sch]
2023-06-21 added 4, 5, 6, 7 pin JST connectors
    [stepper2.kicad_pcb, stepper2.kicad_sch]
2023-07-04 PCB - added VBAT; JST peripherial connectors; power supply capacitors
    [stepper2.kicad_pcb, stepper2.kicad_sch]
2023-07-05 tweaks in PCB and fixed rotated nucleo parts in schematic
    [stepper2.kicad_pcb, stepper2.kicad_sch]
2023-07-05 Added missing limit switch GPIO and button gpio
    [stepper2.kicad_sch]
2023-07-05 DIR and EN pins connected to GPIO
    [stepper2.kicad_pcb, stepper2.kicad_sch]
2023-07-06 First complete version of the PCB
    [stepper2.kicad_pcb, stepper2.kicad_sch]
2023-07-06 Revert to 2 layer PCB
    [stepper2.kicad_pcb, stepper2.kicad_sch]
2023-07-06 minor tweaks on pcb
    [stepper2.kicad_pcb]
2023-07-06 PCB - adjustments and author/date label
    [stepper2.kicad_pcb]
2023-07-06 PCB - minor tweaks
    [stepper2.kicad_pcb]
2023-07-07 PCB - final version sent to JLCPCB
    [stepper2.kicad_pcb, stepper2.kicad_sch]
2023-08-03 fixed mixed labeling for jog buttons; initial config of the NXT timers
    [stepper2.kicad_pcb, stepper2.kicad_sch]
2023-08-09 PCB: NXT/DIR external output connectors and some polishing
    [stepper2.kicad_pcb, stepper2.kicad_sch]
2023-08-09 filtering capacitors for differential receivers; BOM and placement files for SMD elements
    [stepper2-top-pos.csv, stepper2.csv, stepper2.kicad_pcb, stepper2.kicad_sch]
2023-08-10 fixed flipped rotation direction relative to stepper 1
    [stepper2.kicad_pcb, stepper2.kicad_sch]
2023-08-11 Added voltage shifter between FTDI and board
    [stepper2-top-pos.csv, stepper2.csv, stepper2.kicad_pcb, stepper2.kicad_sch]
2023-08-13 universal footprint for UART level shifter
    [stepper2.kicad_pcb, stepper2.kicad_sch, stepper2_BOM.csv, stepper2_CPL.csv]
2023-08-15 prototype of the bottom part of the case
    [bottom.scad, bottom.stl, common.scad]
2023-08-15 updated bottom part of the case
    [bottom.scad, bottom.stl, common.scad]
2023-09-21 minor fixes and optimizations for PCB and bottom case part
    [bottom.scad, common.scad, stepper2.kicad_pcb]
2023-09-30 top part of the case, adjustments to the PCB
    [bottom.scad, common.scad, stepper2.kicad_pcb, stepper2.kicad_sch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]
2023-10-27 corridor added to the case model
    [bottom.stl, common.scad, top.scad, top.stl]
2023-10-27 optimizations in PCB layout made in sync with the design of the case
    [stepper2.kicad_pcb]
2023-10-31 updated footprint of Waveshare USB-UART to prevent solder bridging
    [stepper2.kicad_pcb]
2023-11-06 last fixes and production files for pcb
    [stepper2.kicad_pcb, stepper2.kicad_sch, stepper2_BOM.csv, stepper2_CPL.csv]
2023-11-16 Minor tweaks in the PCB
    [stepper2.kicad_pcb]
2023-11-17 docs added
    [all_render.scad, all_render.stl, bottom.scad, top.scad]
2023-11-17 fixed typo in schematics
    [stepper2.kicad_sch]
2024-02-05 updated BOM and CPL files
    [BOM_stepper2.csv, CPL_stepper2-bottom-pos.csv, CPL_stepper2-top-pos.csv, stepper2-bottom-pos.csv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]
2024-03-02 updated case for new PCB; some minor tweaks
    [all_render.scad, bottom.stl, common.scad, top.scad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]
2024-03-04 manual for soldering
2024-03-08 tuned micro usb hole size in the bottom part of the case
    [bottom.scad, bottom.stl]
2024-03-15 Readme updated with instructions regarding printf and scanf float support
2024-05-10 better order of operations when filtering limit switch readings
2024-10-07 added commands for tmc driver status, tmc EN pin cycle (error reset) and time from boot
2025-07-17 PCB updated to use active and available components; added mpn numbers
    [stepper2.kicad_pcb, stepper2.kicad_sch]
2025-07-17 updated soldering instructions
2025-07-17 reverted DNP flag for 3V battery
    [stepper2.kicad_pcb, stepper2.kicad_sch]
2025-07-17 non-standard components marked as DNP for easier assembly ordering
    [stepper2.kicad_pcb, stepper2.kicad_sch]
2025-08-25 removed old gerber and BOM files, please export from kicad
    [BOM_stepper2.csv, CPL_stepper2-bottom-pos.csv, CPL_stepper2-top-pos.csv, stepper2-bottom-pos.csv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]
2025-08-25 Revise README.md for STM32CubeIDE compilation steps
2025-08-25 Add disclaimer for STM32CubeIDE instructions
2025-08-25 updated symbol for level shifter
    [stepper2.kicad_pcb, stepper2.kicad_sch]
